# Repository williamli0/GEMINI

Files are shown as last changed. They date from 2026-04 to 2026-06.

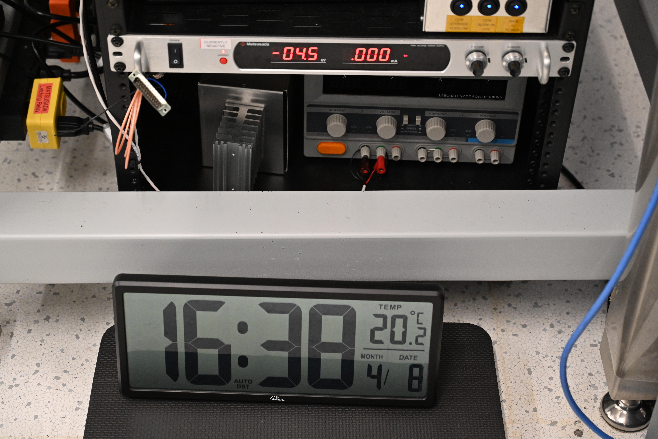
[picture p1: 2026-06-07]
GEMINI-Documents/GEMINI-HV Qualification Testing/260408 Afternoon 4.5 kV/DSC_4537.JPG

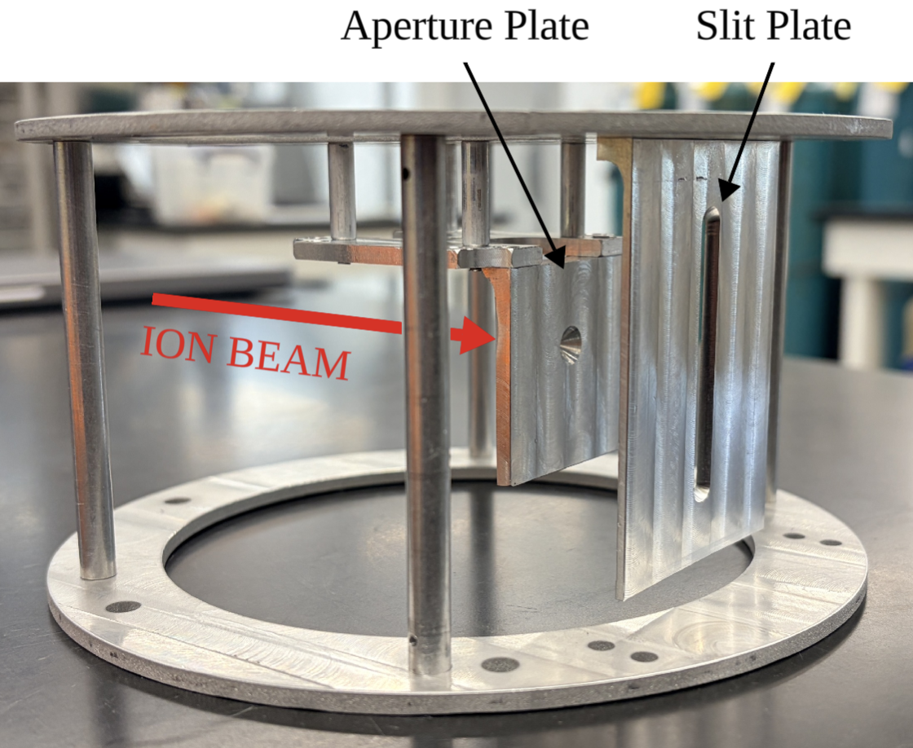
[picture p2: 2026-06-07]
GEMINI-Documents/GEMINI-Photos/GEMINI-JP_Report2Figures/slitPlateMounted.png

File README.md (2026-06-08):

In the SolidWorks folder, GEMINI-00-00-00.SLDASM is the master file that should be opened.

Getting around:

Final reports ("GEMINI-Fall_JP_CORRECTED.pdf" and "WilliamLiMAE399Spring2026Report_File.pdf"), PDR ("Fall 2025 GEMINI PDR.pdf"), and a scan of my engineering notebook ("GEMINI-Notebook") can be found in "GEMINI-Documents"

GEMINI-MATLAB contains the data processing file for GEMINI data: "GEMINIDataPipeline.m"

GEMINI-SIMION contains all the relevant SIMION files for the GEMINI Instrument

GEMINI-Solidworks contains all the necessary CAD files for GEMINI. There are some extraneous files for fasteners and old parts that were not used in the final version.

GEMINI-Drawings contains PDFs of the engineering drawings that were used to manufacture GEMINI.

In "GEMINI-Data", "GEMINI_FirstLightTestPlan.xlsx" contains the test record of two days of GEMINI data collection (configuration of the instrument, beam, notes, etc.). The gain curve file is "MCP Gain Curve Table.docx" found in "JP_Day1_Results" -> "William's GEMINI"

In "GEMINI-Data", "JP_Testing_FullDay1" and "JP_Testing_FullDay1" contain a folder with .csv files from the MCP that should be pointed to in MATLAB for processing. They also contain a folder with the .png output graphs from running the "GEMINIDataPipeline.m" Matlab file.

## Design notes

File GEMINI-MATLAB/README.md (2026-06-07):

GEMINIDataPipeline.m is the main file for processing GEMINI data. It takes in .csv files outputted by the Quantar MCP and outputs the actual visual output of the MCP.

Ensure that the .csv files being processed are on the current Matlab path.

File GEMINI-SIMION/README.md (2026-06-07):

To simulate an electrode in SIMION, a potential array (PA) must be created, either graphically or by means of coding a .GEM file

A .GEM file is the preferred method of creating electrodes because the graphical method is limited to planar, rectangular, or circular symmetry

A .GEM file gives full control over the location and shape of electrodes

After opening SIMION, click "New PA" and "From .GEM File"

Click "Save" and rename the file with extension .pa# which creates a separate numbered .pa file for each electrode programmed in the .GEM file

Click "Refine"

Click "Fast Adjust" to assign voltages to each PA

Then click "View/Open Ion Workbench" and the model is ready to be simulated.

In the .fly2 file, there is a variable at the top of the file that allows you to change the beam energy. It doesn't show up in SIMION when you try to edit the .fly2 file as text so you have to open the .fly2 file in something like Notepad to change the beam energy.

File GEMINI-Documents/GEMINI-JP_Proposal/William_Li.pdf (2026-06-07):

William Li
MAE398 Fall 2025
Adviser: Jamie Rankin

GEMINI: Graphene-Foil Electron-Emission Measurement Investigation for Novel Instrumentation

In space physics, amorphous carbon foils are a standard tool in particle-detecting space instruments because they release secondary electrons when struck by an incident particle. These secondary electrons can be used to make coincidence or time-of-flight (TOF) measurements, which are used by scientists to deduce properties of the incident particle such as mass, species, and energy. However, little is known, beyond a handful of published experiments, about exactly how the process of secondary electron emission works and how foil thickness and composition affect the fluence and energy of secondary electrons.
To address this gap, this proposal aims to develop an ultra-high-vacuum (UHV) compatible scientific instrument that examines the effect of foil thickness and composition on secondary electron emission in a laboratory setting. This laboratory instrument will position a carbon-based foil in a particle beam to measure incident and secondary particles and separate the transmitted particles by charge state. The instrument will be designed based on an existing device built by students in Princeton’s 2023-2024 AST250/251 Space Physics Lab class, which was used to image carbon foils in the path of an ion beam and quantify the number of holes and wrinkles (defects) in the foil and their effect on its performance . The new instrument created as part of this research, GEMINI – which stands for Graphene-Foil Electron-Emission Measurement Investigation for Novel Instrumentation – will hold at least three carbon-based foils, concentrically partition charges, and measure secondary electron emission from the foils, allowing the instrument operator to characterize and perform side-by-side comparisons of amorphous carbon and few-layer-graphene (FLG) foils under the same particle beam. The end scientific goal of this research is to create an empirical model that infers foil thickness and composition based on the fluence and energy of secondary electrons emitted from the foil when it is placed in an incident particle beam.
In current literature it is hypothesized that the thinner the foil, the more sensitive a space instrument will be to detecting higher mass and lower energy particles, so a graphene foil, as a single layer of carbon, is expected to perform significantly better than amorphous carbon. However, existing experimentally-based findings in the literature do not support that theory and show that graphene only has marginal improvements over amorphous carbon. In addition to the carbon layer thickness, it is hypothesized that there is a “crud layer” of water vapor and other trace elements that accumulates on both types of carbon-based foils which significantly increases the thickness and negates the supposed benefits of a thinner foil. The development of GEMINI, will therefore, hold tremendous scientific value. It will mark the first ever study of secondary electron emission as a function of graphene foil thickness and composition and will allow future researchers to reliably characterize different carbon-based foils with varying thicknesses and surface compositions in a laboratory setting, in search for the optimal candidates for space flight. As previously mentioned, GEMINI will build upon an apparatus first designed by the 2023-2024 AST250/251 class. The class’s instrument uses three linear actuators to move a pinhole and carbon foil in front of a microchannel plate (MCP) imager so that when the device is placed in line with a beam of particles in the Space Physics Lab’s vacuum chamber, the MCP

William Li
MAE398 Fall 2025
Adviser: Jamie Rankin

creates a 2D spatial map of particle counts. It also has a metal gate (consisting of 2 parallel rods) that can be energized to high voltage and serves as an electrostatic analyzer (ESA), deflecting particles based on their energy and/or charge. This creates a visual distribution on the MCP which can be used to quantify how many of the particles are negatively charged, positively charged, or neutral, which in turn provides information on the composition of the foil.
Building upon the AST250/251 design, to meet the goals of this research, a channel electron multiplier (CEM) and new electro-optical components will be added to the design to measure the energy and fluence of secondary electrons emitted from the foil. CEMs multiply 1 electron to ~107-108 electrons, essentially creating a cascade of electrons with enough charge to be turned into a detectable signal. Adding a CEM directly contributes to the science goals of GEMINI, as it allows us to investigate how the foil thickness and composition affect the energy and fluence of secondary electron emission as the incident particles interact with the foil. GEMINI also fixes some mechanical flaws with the AST250/251 design, primarily related to the linear actuation method, which cannot precisely control the position of the pinhole and carbon foils as intended and is prone to getting stuck, making the device unreliable. The entire device is also tilted at a 45-degree angle to facilitate retraction of the linear actuators which are only controllable in the extending direction. However, this poses challenges for experimental reproducibility and needs to be re-examined.
For this project, SolidWorks CAD software will be used to mechanically design GEMINI and files from SolidWorks will be exported to Ansys for analysis and SIMION for electro-optical simulations. From an educational development perspective, this independent research is an opportunity to improve CAD skills, specifically in Design for Manufacturing (DFM). This project is also an opportunity to learn how to perform simulations in Ansys, including, but not limited to structural FEA and thermal simulations. Lastly, the project will also provide experience with SIMION, specifically in verifying simulation results by comparing them to collected data.
In total, the project duration spans both the Fall 2025 and Spring 2026 semesters. For Fall 2025 the requirements for this project are to (1) complete the redesign of the existing AST250/251 class instrument, (2) achieve a 15% reduction in mass without increasing the volume of the instrument, and (3) test the instrument and achieve a reliability of 10 cumulative hours in a beamline without a fault. In Spring 2026, with GEMINI built, the focus of the research will shift to taking scientific measurements of amorphous carbon foils and FLGs and creating the model that connects the foil’s thickness and composition properties to the data collected by the instrument. The foils will then be taken to Princeton’s Imaging and Analysis Center (IAC) for foil thickness and composition measurements, in order to quantify the agreement between the model and IAC measurements, with a goal of achieving agreement to within 10%. In terms of project management, this project involves a weekly advisor-student meeting to ensure continuous satisfactory progress, attendance at the Space Physics Lab weekly standup at 8AM on the first day of the week, and scheduled time to work in the lab from 1PM-5PM on Thursdays and 8:30AM-5PM on Fridays.

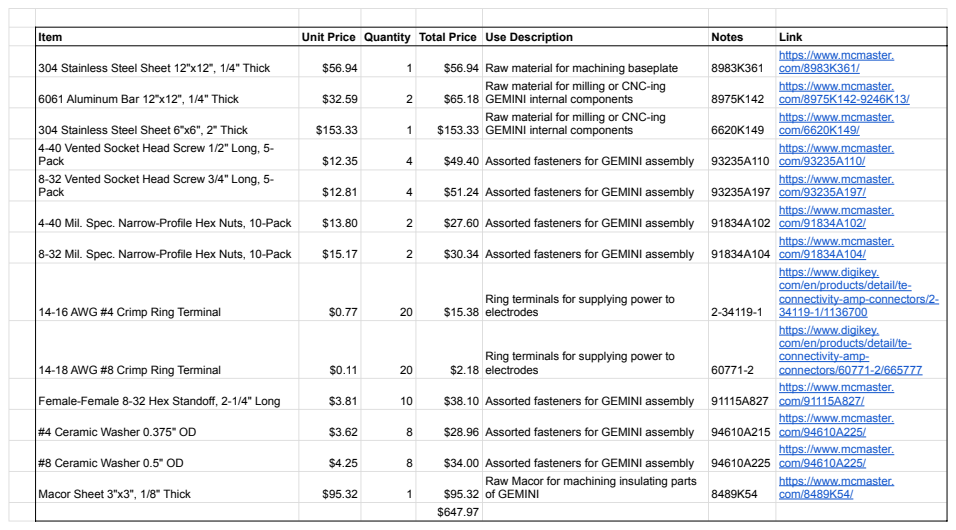
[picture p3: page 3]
Item; Unit Price Quantity Total Price Use Description; Notes; Link; 304 Stainless Steel Sheet 12"x12", 1/4" Thick; $56.94 Raw material for machining baseplate; 6061 Aluminum Bar 12"x12", 1/4" Thick; GEMINI internal components; 304 Stainless Steel Sheet 6"x6", 2" Thick; Pack; $49.40 Assorted fasteners for GEMINI assembly; $51.24 Assorted fasteners for GEMINI assembly; 4-40 Mil. Spec. Narrow-Profile Hex Nuts, 10-Pack; $27.60 Assorted fasteners for GEMINI assembly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

https://www.mcmaster.
com/8983K361/ (https://www.mcmaster.com/8983K361/)
com/8975K142-9246K13/ (https://www.mcmaster.com/8975K142-9246K13/)
com/6620K149/ (https://www.mcmaster.com/6620K149/)
com/93235A110/ (https://www.mcmaster.com/93235A110/)
com/93235A197/ (https://www.mcmaster.com/93235A197/)
com/91834A102/ (https://www.mcmaster.com/91834A102/)
com/91834A104/ (https://www.mcmaster.com/91834A104/)
https://www.digikey.
com/en/products/detail/te-
connectivity-amp-connectors/2-
connectivity-amp-
connectors/60771-2/665777 (https://www.digikey.com/en/products/detail/te-connectivity-amp-connectors/60771-2/665777)
com/91115A827/ (https://www.mcmaster.com/91115A827/)
com/94610A225/ (https://www.mcmaster.com/94610A225/)
com/8489K54/ (https://www.mcmaster.com/8489K54/)

Raw material for milling or CNC-ing

4-40 Vented Socket Head Screw 1/2" Long, 5-
8-32 Vented Socket Head Screw 3/4" Long, 5-

Ring terminals for supplying power to

Raw Macor for machining insulating parts

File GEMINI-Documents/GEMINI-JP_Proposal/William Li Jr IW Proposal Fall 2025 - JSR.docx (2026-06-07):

GEMINI: Graphene-Foil Electron-Emission Mapping Investigation for Novel Instrumentation

In space physics, amorphous carbon foils are a standard tool in particle-detecting space instruments because they release secondary electrons when struck by an incident particle. These secondary electrons can be used to make coincidence or time-of-flight (TOF) measurements, which are used by scientists to deduce properties of the incident particle such as mass, species, and energy. However, little is known beyond a handful of published experiments, about exactly how the process of secondary electron emission works and how foil thickness and composition affect the fluence of secondary electrons.

To address this gap, this proposal aims to develop an ultra-high-vacuum (UHV) compatible scientific instrument that holds a carbon foil in the path of a particle beam and partitions particles passing through the foil based on charge state while measuring the fluence of secondary electrons emitted from the carbon foil as it interacts with the beam. The instrument will be designed based on an existing device built by students in the 2023-2024 AST250/251 class which was used to image carbon foils in the path of an ion beam and quantify the effect of holes and wrinkles (defects) in the foil on its performance. The new instrument created as part of this research will hold at least three carbon-based foils, concentrically partition charges, and measure secondary electron emission from the foils allowing the instrument operator to measure the effect of different types of foils, such as amorphous carbon foils and few-layer-graphene foils (FLGs) under the same particle beam. The end scientific goal of this research is to create an empirical model that infers the thickness and composition of the measured carbon-based foil based on the fluence of secondary electrons emitted from the foil.

In current literature it is hypothesized that the thinner the foil, the more sensitive a space instrument will be to detecting higher mass particles and lower energy particles, so a graphene foil, as a single layer of carbon, should perform significantly better than amorphous carbon. However, existing experimentally-based findings in the literature does not support that theory and shows that graphene only has marginal improvements over amorphous carbon. It is hypothesized that there is a “crud layer” of water vapor and other trace elements that accumulates on carbon-based foils which significantly increases the thickness and erases the supposed benefits of a thinner foil. In a laboratory setting, future researchers can use GEMINI to test different graphene foils with varying thicknesses and surface compositions to search for the optimal graphene foil for space flight. The development of GEMINI holds tremendous scientific value. It will mark the first ever study of secondary electron emission as a function of graphene foil thickness and composition and thus will inform the qualification of graphene foils as the next generation of carbon foils in space instruments.

As previously mentioned, this project will build upon an apparatus first designed by the 2023-2024 AST250/251 class in the Space Physics Lab. The class’s instrument uses three linear actuators to move a pinhole and carbon foil in front of a microchannel plate (MCP) imager so that when the device is placed in line with a beam of particles in the Space Physics Lab’s vacuum chamber, the MCP creates a 2D spatial map of particle counts. It also has a metal gate (consisting of 2 parallel rods) that can be energized to high voltage and serves as an electrostatic analyzer (ESA), deflecting particles based on their energy and charge. This creates a visual distribution on the MCP which can be used to quantify how many of the particles emitted from the foil came off as negatively charged, positively charged, or neutral, as well as how much charge they carried (+1, +2, etc.). The ESA gate can also filter out particles to only look at one specific energy at a time.

There are some flaws with the AST250/251 design that primarily relate to the actuation method, which cannot precisely control the position of the pinhole and carbon foils as intended and is prone to getting stuck, making the device unreliable. The entire device is also tilted at a 45-degree angle to facilitate retraction of the linear actuators which are only controllable in the extending direction, which poses challenges for experimental reproducibility and also needs to be re-examined. GEMINI will improve upon the AST250/251 instrument mechanically by implementing a different actuation mechanism, possibly a rotating wheel rather than linear actuators. A new concentric ESA will also be designed to replace the existing metal gate ESA because the metal gate design shapes the paths of ions in a rectangular pattern, resulting in lost data when the particles collide with the MCP which has a circular aperture. Building upon the AST250/251 design, to meet the goals of this research, a channel electron multiplier (CEM) and new ion optics will be added to the design to take secondary electron measurements. CEMs multiply 1 electron to ~10⁷-10⁸ electrons, essentially creating a cascade of electrons with enough charge to be turned into a detectable signal.

For this project, SolidWorks CAD software will be used to mechanically design GEMINI and files from SolidWorks will be exported to Ansys for analysis and SIMION for electro-optical simulations. From an educational development perspective, this independent research is an opportunity to improve CAD skills, specifically in Design for Manufacturing (DFM). This project is also an opportunity to learn how to perform simulations in Ansys, including, but not limited to structural FEA and thermal simulations. Lastly, the project will also provide experience with SIMION, specifically in verifying simulation results by comparing them to collected data.

In total, the project duration spans both the Fall 2025 and Spring 2026 semesters. For Fall 2025 the requirements for this project are to (1) complete the redesign of the existing AST250/251 class instrument, (2) achieve a 15% reduction in mass without increasing the volume of the instrument, and (3) test the instrument and achieve a reliability of 10 cumulative hours in a beamline without a fault. In Spring 2026, with the instrument built, the focus of the research will shift to taking scientific measurements of amorphous carbon foils and FLGs and creating the model that connects the foil’s thickness and composition properties to the data collected by the instrument. The foils will then be taken to Princeton’s Imaging and Analysis Center (IAC) for foil thickness and composition measurements, in order to quantify the agreement between the model and IAC measurements, with a goal of achieving agreement to within 10%.

In terms of project management, this research involves a weekly advisor-student meeting to ensure continuous satisfactory progress, attendance at the Space Physics Lab weekly standup at 8AM on the first day of the week, and scheduled time to work in the lab from 1PM-5PM on Thursdays and 8:30AM-5PM on Fridays.

William Li MAE398, Fall 2025 Adviser: Jamie Rankin

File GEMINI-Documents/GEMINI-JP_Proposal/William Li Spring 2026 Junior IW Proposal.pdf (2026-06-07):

William Li
MAE399 Spring 2026
Adviser: Jamie Rankin

GEMINI: Graphene-Foil Electron-Emission Measurement Investigation for Novel Instrumentation

Amorphous carbon foils (~20-30 atomic layers in thickness) are a crucial piece of any scientific space instrument that seeks to study the solar wind or other particles present in the solar system. This is because carbon foils possess the property of releasing a secondary electron when struck by an incident particle, usually an ion. This secondary electron can be used to make coincidence or time-of-flight (TOF) measurements, which, combined with other parameters, enables scientists to deduce properties of the incident particle such as the mass, species, and energy. However, carbon foils also affect the incident particle in undesirable ways, by causing angular scattering and energy loss of the particle. It is theorized that thinner foils are able to detect lower energy particles and higher mass particles because they reduce angular scattering and energy loss, but the exact relationship between foil thickness and these other properties are not well understood. For example, previous studies have shown that the proportionality between foil thickness and angular scattering is different for carbon foils and graphene (a single atomic layer of carbon) foils, but these studies did not explore energies lower than 3 keV. In the Fall 2025 semester, the GEMINI instrument was designed to measure angular scattering and secondary electron emission of carbon and graphene foils at energies ranging from 200 eV to 2.5 keV. This Spring 2026 independent work is a continuation of the work completed in Fall 2025. This proposal for Spring 2026 independent work proposes placing the GEMINI instrument in the Science Vacuum Chamber in the Princeton Space Physics Lab and exposing it to a variety of ion beams to gather data on the energy and yield of secondary electrons from graphene and carbon foils at ion beam energies of 200 eV to 2.5 keV. This fills a gap in existing literature exploring the angular scattering and secondary electron emission of graphene foils at low energy ion beams. The scope of work for the Spring 2026 semester includes machining the components of GEMINI, physically assembling it, and testing it in vacuum in the Space Physics Lab. For testing, GEMINI was designed to hold three carbon or graphene foils at once so that direct comparisons can be made between the different foils without having to remove the instrument from the vacuum chamber. Essentially, an identical ion beam can be used to study three different foils. For this semester, the three foils that will be tested in GEMINI are a graphene foil, 0.6 μg/cm² carbon foil, and 1.1 μg/cm² carbon foil. Each of the foils will be exposed to an ion beam of energies ranging from 200 eV to 2.5 keV in 100 eV increments. The beam compositions that will be tested are H

+
, H2

+

, He⁺

, and Ar⁺
. The scope of work for Spring 2026 also encompasses developing a data collection and processing pipeline for GEMINI. This involves writing LabVIEW code to automate the process of imaging each of the three foils on GEMINI with different beam compositions and energies. MATLAB will be used to process the data from GEMINI’s primary sensor, the imaging microchannel plate (MCP).
Long-term, the goal is to continue using GEMINI to contribute to heliophysicists’ understanding of graphene foils by modifying the thickness and composition of graphene foils on the molecular scale and studying how different modifications affect angular scattering, energy loss, and secondary electron emission from graphene foils. This is future research that will be pursued in the 2026-2027 academic year.

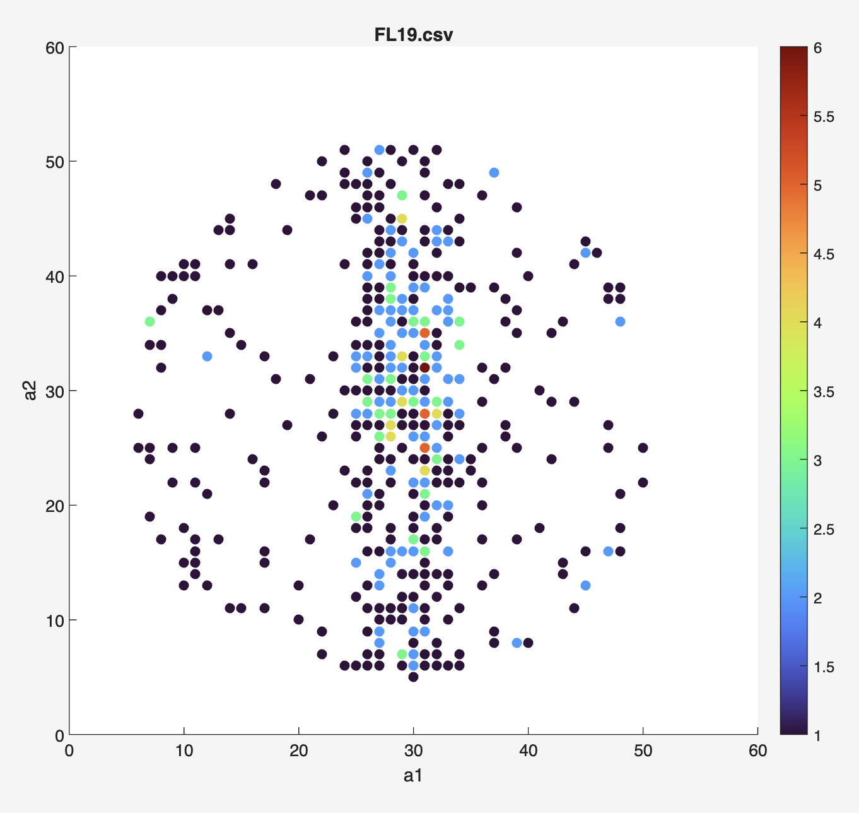
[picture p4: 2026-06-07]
GEMINI-Documents/GEMINI-Photos/GEMINI-JP_Report2Figures/Screenshot 2026-04-23 at 14.20.40.png

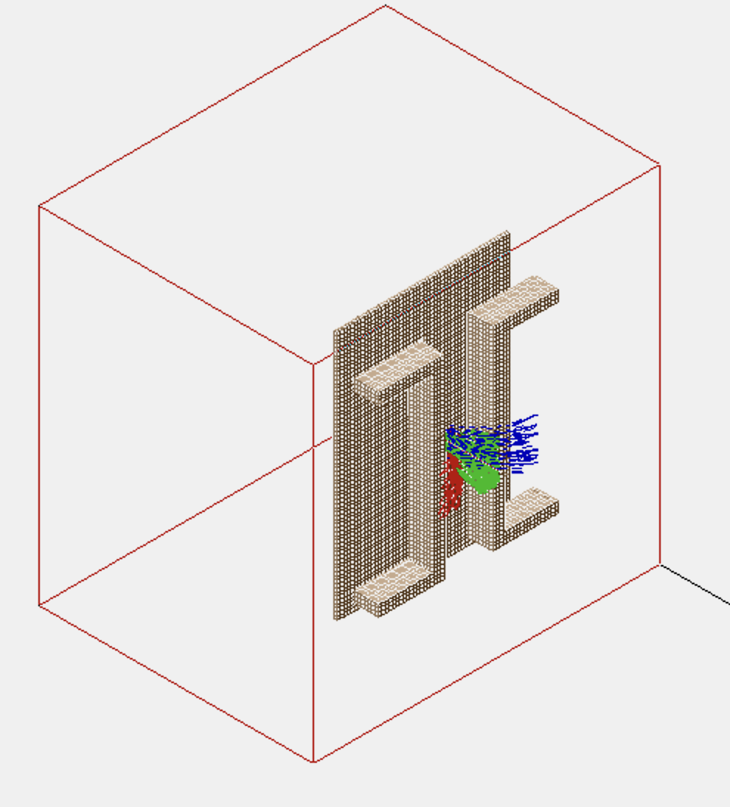
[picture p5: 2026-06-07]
GEMINI-Documents/GEMINI-Photos/GEMINI-JP_Report2Figures/500eV_600V_p_Iso.png

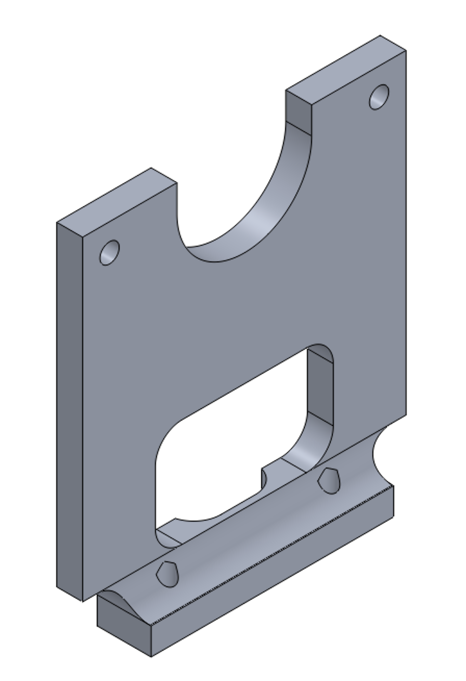
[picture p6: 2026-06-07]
GEMINI-Documents/GEMINI-Photos/GEMINI-JP_Report2Figures/Screenshot 2026-04-28 at 16.29.42.png

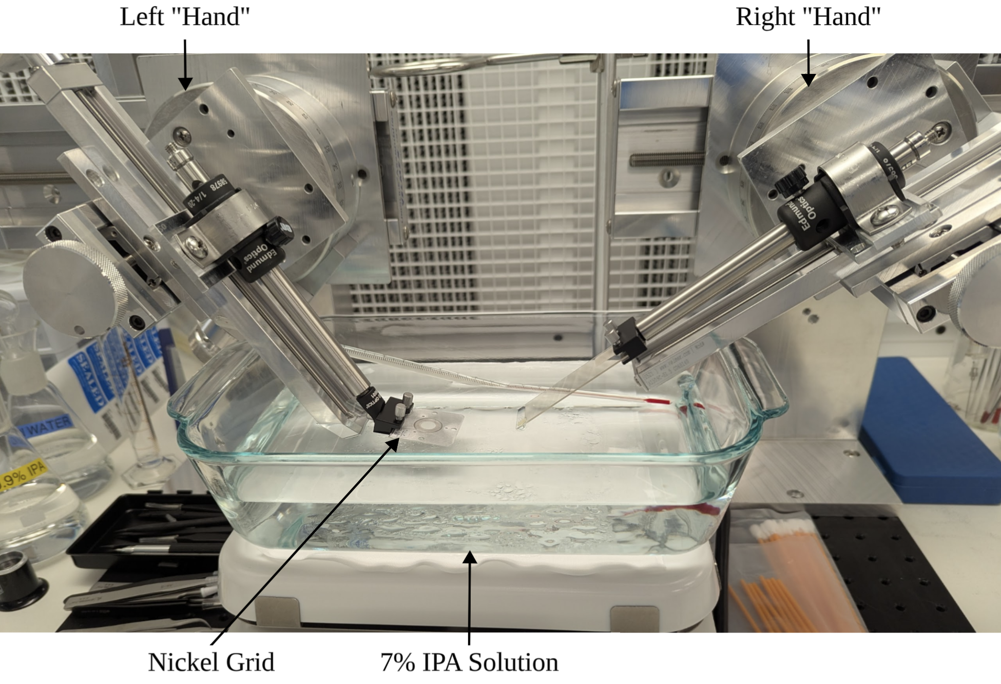
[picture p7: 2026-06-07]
GEMINI-Documents/GEMINI-Photos/GEMINI-JP_Report2Figures/floatApparatus.png

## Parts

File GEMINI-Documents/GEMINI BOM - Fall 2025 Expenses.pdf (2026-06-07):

# GEMINI Bill of Materials

ITEM
NO.

PART

| NO. | DESCRIPTION | ORDER
| | | QTY | UNIT
| | | | PRICE | TOTAL
| | | | | PRICE | DATE
| | | | | | ORDERED | COMMENTS
1 | 93505A027 | 10-32, 1-1/4" Long Male-Female Hex
| | Standoff | 5 | $1.38 | $6.90 | 12/8/25
2 | 92510A648 | #10 7/8" Long Aluminum Unthreaded Spacer | 5 | $1.74 | $8.70 | 12/8/25
3 | 93330A541 | 4-40, 3" Long, Aluminum Female-Female
| | Round Standoff | 4 | $1.52 | $6.08 | 12/8/25 | Roof Mounting to Upper Outer Skirt
4 | 94335A115 | 6-32, 1/2" Long, Glazed L5 Ceramic Female-
| | Female Round Standoff | 4 | $5.65 | $22.60 | 12/8/25 | Deflector Plate Mounting Standoffs
5 | Shipping 1 | Shipping to E-Quad Loading Dock | 1 | $9.21 | $0.00 | 12/8/25
6 | 89015K259 | 6061 Aluminum Sheet 0.160" Thick, 8" x 8" | 4 | $19.49 | $77.96 | 1/28/26 | Roof, Upper Outer Skirt
7 | 89015K255 | 6061 Aluminum Sheet 0.160" Thick, 6" x 6" | 1 | $12.47 | $12.47 | 1/28/26 | Inner Skirt
8 | 89155K221 | Oversized 6061 Aluminum Sheet 1/4" Thick, 8" x 8" | 2 | $17.06 | $34.12 | 1/28/26 | All other parts except Deflector Plates
9 | 8975K613 | 6061 Aluminum Bar 5/16" Thick x 1" Wide x 12'' Long | 1 | $4.18 | $4.18 | 1/28/26 | 3.6'' required. Deflector Plates. Ordered 8976K856 (same)
10 | 92196A103 | 4-40, 1/8" Long, 18-8 SS Socket Head Screw. Pack of 100 | 1 | $6.10 | $6.10 | 1/28/26 | Shield mounting and Deflector Plate power.
11 | 90550A122 | M4 x 0.7 mm, 10 mm Long, 18-8 SS Vented Flat Head Screw. Pack of 5 | 1 | $13.10 | $13.10 | 1/28/26 | Inner Skirt mounting to Rotational Stage
12 13 | 93330A541 94335A115 | 4-40, 3" Long, Aluminum Female-Female Round Standoff | 2 | $2.17 | $4.34 | 1/28/26 | Roof Mounting to Upper Outer Skirt
| | 6-32, 1/2" Long, Glazed L5 Ceramic Female-Female Round Standoff | 2 | $5.65 | $11.30 | 1/28/26 | Deflector Plate Mounting Standoffs
14 | 92510A460 | #8, 1/8" Long Aluminum Unthreaded Spacer | 8 | $0.37 | $2.96 | 1/28/26 | For raising Inner Skirt
15 | 88805A27 | 1/4" Ball End Mill, Uncoated Carbide, 4 Flute, 2-1/2" Overall Length | 1 | $20.85 | $20.85 | 1/28/26 | For machining fillets
16 | 2739A38 | 90 Degree Fluteless Smooth-Finish Countersink | 1 | $15.40 | $15.40 | 1/28/26 | For Inner Skirt M4 countersinks
17 | 2739A33 | 82 Degree Fluteless Smooth-Finish Countersink | 1 | $15.40 | $15.40 | 1/28/26 | For all other countersinks
18 | 92210A105 | 4-40, 1/4" Long, 18-8 SS Flat Head Screw 82 Degree Countersink. Pack of 100 | 1 | $4.43 | $4.43 | 1/28/26 | Workhorse. Standard fastener for most of GEMINI
19 | 91292A322 | M5 x 0.8 mm, 110 mm Long, 18-8 SS Socket Head Screw. Pack of 10 | 1 | $11.03 | $11.03 | 1/28/26 | For mounting Upper Outer Skirt to Rotational Stage
20 | Shipping 2 | Shipping to E-Quad Loading Dock | 1 | $12.10 | $0.00 | 1/28/26
21 | 8974K105 | 6061 Aluminum Rod 3/16" Diameter x 1/2 Foot Long | 1 | $1.60 | $1.60 | 1/29/26 | 0.687'' each (x4). Dummy hardware for when motor is detached. Ordered 8974K21 (same)
22 | 92125A138 | M3 x 0.5 mm, 25 mm Long, 18-8 SS Flat Head Screw. Pack of 100 | 1 | $11.38 | $11.38 | 1/29/26 | Require 4. Dummy hardware for when motor is detached
23 | 93033A107 | M3 x 0.5 mm 18-8 SS Flange Nut. Pack of 100 | 1 | $7.33 | $7.33 | 1/29/26 | For mounting D42.1 Motor
24 | 91979A207 | 2-56, 1/8" Long, 18-8 SS Set Screw. Pack of 10 | 1 | $6.79 | $6.79 | 1/29/26 | For Aperture Rotation Plate
25 | 92510A435 | #12, 2-1/4" Long Aluminum Unthreaded Spacer | 5 | $7.73 | $38.65 | 1/29/26 | For mounting Upper Outer Skirt to Rotational Stage
26 | Shipping 3 | Shipping to E-Quad Loading Dock | 1 | $10.18 | $0.00 | 1/29/26
TOTAL: | $343.67

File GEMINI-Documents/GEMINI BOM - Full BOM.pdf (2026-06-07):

# GEMINI Bill of Materials

ITEM NO. | PART NO. | DESCRIPTION | REQ. QTY | ORDER QTY | UNIT PRICE | TOTAL PRICE | COMMENTS
1 | 89015K259 | 6061 Aluminum Sheet 0.160" Thick, 8" x 8" | 3 | 4 | $19.49 | $77.96 | Roof, Upper Outer Skirt
2 | 89015K255 | 6061 Aluminum Sheet 0.160" Thick, 6" x 6" | 1 | 1 | $12.47 | $12.47 | Inner Skirt
3 | 89155K221 | Oversized 6061 Aluminum Sheet 1/4" Thick, 8" x 8" | 1 | 2 | $17.06 | $34.12 | All other parts except Deflector Plates
4 | 8975K613 | 6061 Aluminum Bar 5/16" Thick x 1" Wide x 12'' Long | 1 | 1 | $4.18 | $4.18 | 3.6'' required. Deflector Plates. Ordered 8976K856 (same)
5 | 92196A103 | 4-40, 1/8" Long, 18-8 SS Socket Head Screw. Pack of 100 | 14 | 1 | $6.10 | $6.10 | Shield mounting and Deflector Plate power.
6 | 90550A122 | M4 x 0.7 mm, 10 mm Long, 18-8 SS Vented Flat Head Screw. Pack of 5 | 4 | 1 | $13.10 | $13.10 | Inner Skirt mounting to Rotational Stage
7 | 93330A541 | 4-40, 3" Long, Aluminum Female-Female Round Standoff | 4 | 6 | $2.17 | $13.02 | Roof Mounting to Upper Outer Skirt. Ordered 4 on 12/8/25
8 | 94335A115 | 6-32, 1/2" Long, Glazed L5 Ceramic Female-Female Round Standoff | 4 | 6 | $5.65 | $33.90 | Deflector Plate Mounting Standoffs. Ordered 4 on 12/8/25
9* | 7113K148 | 22-18 Wire Gauge, #4 Screw Size, Tin-Plated Copper Ring Terminals Noninsulated. Pack of 100 | 2 | 1 | $16.02 | $16.02 | Power delivery to Deflector Plates.
10* | 92210A077 | 2-56, 1/4" Long, 18-8 SS Flat Head Screw 82 Degree Countersink. Pack of 100 | 4 | 1 | $5.83 | $5.83 | For mounting Aperture Plates
11* | 92210A105 | 4-40, 1/4" Long, 18-8 SS Flat Head Screw 82 Degree Countersink. Pack of 100 | 18 | 1 | $4.43 | $4.43 | Workhorse. Standard fastener for most of GEMINI. Ordered anyways (unsure of lab qty)
12* | 93235A144 | Vented Socket Head Screw 6-32 Thread Size, 1/4" Long. Pack of 5 | 8 | 2 | $5.97 | $11.94 | For Deflector Plate ceramic standoffs
13 | 92510A460 | #8, 1/8" Long Aluminum Unthreaded Spacer | 4 | 8 | $0.38 | $3.04 | For raising Inner Skirt
14 | 8974K105 | 6061 Aluminum Rod 3/16" Diameter x 1/2 Foot Long | 1 | 1 | $1.60 | $1.60 | 0.687'' each (x4). Dummy hardware for when motor is detached. Ordered 8974K21 (same)
15 | 92125A138 | M3 x 0.5 mm, 25 mm Long, 18-8 SS Flat Head Screw. Pack of 100 | 4 | 1 | $11.38 | $11.38 | Require 4. Dummy hardware for when motor is detached
16 | 8803A383 | 0.1985" Reamer, High-Speed Steel | 1 | 1 | $24.52 | $24.52 | For creating Aperture Rotation Plate collar hole
17 | 93033A107 | M3 x 0.5 mm 18-8 SS Flange Nut. Pack of 100 | 4 | 1 | $7.33 | $7.33 | For mounting D42.1 Motor
18 | 91979A207 | 2-56, 1/8" Long, 18-8 SS Set Screw. Pack of 10 | 1 | 1 | $6.79 | $6.79 | For Aperture Rotation Plate
19 | 92510A435 | #12, 2-1/4" Long Aluminum Unthreaded Spacer | 5 | 5 | $7.73 | $38.65 | For mounting Upper Outer Skirt to Rotational Stage
20 | 91292A322 | M5 x 0.8 mm, 110 mm Long, 18-8 SS Socket Head Screw. Pack of 10 | 5 | 1 | $11.03 | $11.03 | For mounting Upper Outer Skirt to Rotational Stage
21 | 88805A27 | 1/4" Ball End Mill, Uncoated Carbide, 4 Flute, 2-1/2" Overall Length | 1 | 1 | $20.85 | $20.85 | For machining fillets
22 | 2739A38 | 90 Degree Fluteless Smooth-Finish Countersink | 1 | 1 | $15.40 | $15.40 | For Inner Skirt M4 countersinks
23 | 2739A33 | 82 Degree Fluteless Smooth-Finish Countersink | 1 | 1 | $15.40 | $15.40 | For all other countersinks
TOTAL: | $389.06

* indicates part already exists in the Space Physics Lab

# GEMINI Bill of Materials (Continued)

OTHER COMPONENTS (INFRASTRUCTURE & NON-CRITICAL)

ITEM NO. | PART NO. | DESCRIPTION | REQ. QTY | ORDER QTY | UNIT PRICE | TOTAL PRICE | COMMENTS
23 | D42.1-H | AML UHV Stepper Motor. Dry, lubricated hybrid ceramic bearings | 1 | 1 | $1,080 | $1,080 | For rotating aperture plates
24 | SMD3 | AML Single-Axis Bipolar Stepper Motor Drive | 1 | 1 | $840 | $840 | For controlling D42.1-H motor
25* | 3394A | Quantar 2-Layer 40 mm MCP | 1 | 0 | N/A | N/A
26* | | MCP #0 Mounting Screws | 4 | 0 | N/A | N/A | For mounting MCP
27* | | RV120 Rotational Stage | 1 | 0 | N/A | N/A
28* | | CoDICE 0.9895'' Spacer | 1 | 0 | N/A | N/A
29* | | 0.010'' Thick Aluminum Shim Stock | 1 | 0 | N/A | N/A | For Shield and CoDICE Spacer Shim
30* | | SHV5 Connector | 2 | 0 | N/A | N/A
31* | | High Voltage insulated wiring | | 0 | N/A | N/A
32* | | High Voltage Power Supply | 2 | 0 | N/A | N/A | For Deflector Plates
33* | | Low Voltage Power Supply | 1 | 0 | N/A | N/A | For Deflector Plates measuring secondary electrons
TOTAL: | $1,920

* indicates part already exists in the Space Physics Lab

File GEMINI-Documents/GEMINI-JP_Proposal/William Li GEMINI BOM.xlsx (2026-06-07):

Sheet: Fall 2025
Item | Unit Price | Quantity | Total Price | Use Description | Notes | Link
304 Stainless Steel Sheet 12"x12", 1/4" Thick | $56.94 | 1 | $56.94 | Raw material for machining baseplate | 8983K361 | https://www.mcmaster.com/8983K361/
6061 Aluminum Bar 12"x12", 1/4" Thick | $32.59 | 2 | $65.18 | Raw material for milling or CNC-ing GEMINI internal components | 8975K142 | https://www.mcmaster.com/8975K142-9246K13/
304 Stainless Steel Sheet 6"x6", 2" Thick | $153.33 | 1 | $153.33 | Raw material for milling or CNC-ing GEMINI internal components | 6620K149 | https://www.mcmaster.com/6620K149/
4-40 Vented Socket Head Screw 1/2" Long, 5-Pack | $12.35 | 4 | $49.40 | Assorted fasteners for GEMINI assembly | 93235A110 | https://www.mcmaster.com/93235A110/
8-32 Vented Socket Head Screw 3/4" Long, 5-Pack | $12.81 | 4 | $51.24 | Assorted fasteners for GEMINI assembly | 93235A197 | https://www.mcmaster.com/93235A197/
4-40 Mil. Spec. Narrow-Profile Hex Nuts, 10-Pack | $13.80 | 2 | $27.60 | Assorted fasteners for GEMINI assembly | 91834A102 | https://www.mcmaster.com/91834A102/
8-32 Mil. Spec. Narrow-Profile Hex Nuts, 10-Pack | $15.17 | 2 | $30.34 | Assorted fasteners for GEMINI assembly | 91834A104 | https://www.mcmaster.com/91834A104/
14-16 AWG #4 Crimp Ring Terminal | $0.77 | 20 | $15.38 | Ring terminals for supplying power to electrodes | 2-34119-1 | https://www.digikey.com/en/products/detail/te-connectivity-amp-connectors/2-34119-1/1136700
14-18 AWG #8 Crimp Ring Terminal | $0.11 | 20 | $2.18 | Ring terminals for supplying power to electrodes | 60771-2 | https://www.digikey.com/en/products/detail/te-connectivity-amp-connectors/60771-2/665777
Female-Female 8-32 Hex Standoff, 2-1/4" Long | $3.81 | 10 | $38.10 | Assorted fasteners for GEMINI assembly | 91115A827 | https://www.mcmaster.com/91115A827/
#4 Ceramic Washer 0.375" OD | $3.62 | 8 | $28.96 | Assorted fasteners for GEMINI assembly | 94610A215 | https://www.mcmaster.com/94610A225/
#8 Ceramic Washer 0.5" OD | $4.25 | 8 | $34.00 | Assorted fasteners for GEMINI assembly | 94610A225 | https://www.mcmaster.com/94610A225/
Macor Sheet 3"x3", 1/8" Thick | $95.32 | 1 | $95.32 | Raw Macor for machining insulating parts of GEMINI | 8489K54 | https://www.mcmaster.com/8489K54/
 |  |  | $647.97

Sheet: Spring 2026
Item | Unit Price | Quantity | Total Price | Use Description | Notes | Link
 |  |  | $0.00
 |  |  | $0.00
 |  |  | $0.00
 |  |  | $0.00
 |  |  | $0.00
 |  |  | $0.00
 |  |  | $0.00
 |  |  | $0.00
 |  |  | $0.00
 |  |  | $0.00
 |  |  | $0.00
 |  |  | $0.00
 |  |  | $0.00
 |  |  | $0.00
 |  |  | $0.00
 |  |  | $0.00
 |  |  | $0.00

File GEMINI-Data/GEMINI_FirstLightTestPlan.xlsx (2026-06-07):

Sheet: Day 1 Test Plan
Date | Start Time (EST) | Stop Time (EST) | GEMINI Operator Name | Facility Operator Name | ACTIONS / STATUS | Filename | Converted Filename | Procedure/HV log | Test Objective | Foil | North Deflector Voltage (V) | South Deflector Voltage (V) | MCP Voltages (V) | IS Pressure (Torr) | IT Pressure (Torr) | Focus 1 | Focus 2 | Emission current (mA) | Ext (%) | Px (mm) | Py (mm) | Wien Filter Plate Potential | Energy | Ion Source Energy & Species | Helmholtz Coil Voltage (V) | Helmholtz Coil Current (A) | Helmholtz Coil Status (On/Off) | Rotational Stage (Axis 2) (deg) | Linear Stage (Axis 3) | SC Gate Valve | MC Gate Valve | Science Chamber Pressure (Torr) | Main Chamber Pressure (Torr) | Comments
 |  |  |  |  |  | GFL0 | GEMINI_p1000_FirstLight |  | First Light | None | +0 | +0 |  |  |  |  |  |  |  |  |  |  |  | 1 keV p+ |  |  | On | 0 | 0
 |  |  |  |  |  | p1 | GEMINI_p1000_N |  | 1 keV p+ Angular Scattering Baseline | None | +1084 | -+1084 |  |  |  |  |  |  |  |  |  |  |  | 1 keV p+ |  |  | On | 0 | 0
 |  |  |  |  |  | p2 | GEMINI_p1000_C |  | 1 keV p+ Carbon Angular Scattering | 1.1 ug/cm^2 | +1084 | -+1084 |  |  |  |  |  |  |  |  |  |  |  | 1 keV p+ |  |  | On | 54.12 | 0
 |  |  |  |  |  | p3 | GEMINI_p1000_G |  | 1 keV p+ Graphene Angular Scattering | Graphene | +1084 | -+1084 |  |  |  |  |  |  |  |  |  |  |  | 1 keV p+ |  |  | On | -54.12 | 0
 |  |  |  |  |  | p4 | GEMINI_p1250_N |  | 1.25 keV p+ Angular Scattering Baseline | None | +1355 | -+1355 |  |  |  |  |  |  |  |  |  |  |  | 1.25 keV p+ |  |  | On | 0 | 0
 |  |  |  |  |  | p5 | GEMINI_p1250_C |  | 1.25 keV p+ Carbon Angular Scattering | 1.1 ug/cm^2 | +1355 | -+1355 |  |  |  |  |  |  |  |  |  |  |  | 1.25 keV p+ |  |  | On | 54.12 | 0
 |  |  |  |  |  | p6 | GEMINI_p1250_G |  | 1.25 keV p+ Graphene Angular Scattering | Graphene | +1355 | -+1355 |  |  |  |  |  |  |  |  |  |  |  | 1.25 keV p+ |  |  | On | -54.12 | 0
 |  |  |  |  |  | p7 | GEMINI_p1500_N |  | 1.5 keV p+ Angular Scattering Baseline | None | +1626 | -+1626 |  |  |  |  |  |  |  |  |  |  |  | 1.5 keV p+ |  |  | On | 0 | 0
 |  |  |  |  |  | p8 | GEMINI_p1500_C |  | 1.5 keV p+ Carbon Angular Scattering | 1.1 ug/cm^2 | +1626 | -+1626 |  |  |  |  |  |  |  |  |  |  |  | 1.5 keV p+ |  |  | On | 54.12 | 0
 |  |  |  |  |  | p9 | GEMINI_p1500_G |  | 1.5 keV p+ Graphene Angular Scattering | Graphene | +1626 | -+1626 |  |  |  |  |  |  |  |  |  |  |  | 1.5 keV p+ |  |  | On | -54.12 | 0
 |  |  |  |  |  | p10 | GEMINI_p750_N |  | 750 eV p+ Angular Scattering Baseline | None | +813 | -+813 |  |  |  |  |  |  |  |  |  |  |  | 750 eV p+ |  |  | On | 0 | 0
 |  |  |  |  |  | p11 | GEMINI_p750_C |  | 750 eV p+ Carbon Angular Scattering | 1.1 ug/cm^2 | +813 | -+813 |  |  |  |  |  |  |  |  |  |  |  | 750 eV p+ |  |  | On | 54.12 | 0
 |  |  |  |  |  | p12 | GEMINI_p750_G |  | 750 eV p+ Graphene Angular Scattering | Graphene | +813 | -+813 |  |  |  |  |  |  |  |  |  |  |  | 750 eV p+ |  |  | On | -54.12 | 0
 |  |  |  |  |  | p13 | GEMINI_p_500_N |  | 500 eV p+ Angular Scattering Baseline | None | +542 | -+542 |  |  |  |  |  |  |  |  |  |  |  | 500 eV p+ |  |  | On | 0 | 0
 |  |  |  |  |  | p14 | GEMINI_p_500_C |  | 500 eV p+ Carbon Angular Scattering | 1.1 ug/cm^2 | +542 | -+542 |  |  |  |  |  |  |  |  |  |  |  | 500 eV p+ |  |  | On | 54.12 | 0
 |  |  |  |  |  | p15 | GEMINI_p500_G |  | 500 eV p+ Graphene Angular Scattering | Graphene | +542 | -+542 |  |  |  |  |  |  |  |  |  |  |  | 500 eV p+ |  |  | On | -54.12 | 0
 |  |  |  |  | Disconnect Deflector Plates from HVPS. Connect North Deflector to small blue LVPS | e1 | GEMINI_p1000_N_e |  | 500 eV p+ Secondary Electron Baseline | None | +5 | +0 |  |  |  |  |  |  |  |  |  |  |  | 500 eV p+ |  |  | On | 0 | 0
 |  |  |  |  |  | e2 | GEMINI_p1000_C_e |  | 500 eV p+ Carbon Secondary Electron | 1.1 ug/cm^2 | +5 | +0 |  |  |  |  |  |  |  |  |  |  |  | 500 eV p+ |  |  | On | 54.12 | 0
 |  |  |  |  |  | e3 | GEMINI_p1000_G_e |  | 500 eV p+ Graphene Secondary Electron | Graphene | +5 | +0 |  |  |  |  |  |  |  |  |  |  |  | 500 eV p+ |  |  | On | -54.12 | 0
 |  |  |  |  |  | e4 | GEMINI_p1250_N_e |  | 750 eV p+ Secondary Electron | None | +5 | +0 |  |  |  |  |  |  |  |  |  |  |  | 750 eV p+ |  |  | On | 0 | 0
 |  |  |  |  |  | e5 | GEMINI_p1250_C_e |  | 750 eV p+ Carbon Secondary Electron | 1.1 ug/cm^2 | +5 | +0 |  |  |  |  |  |  |  |  |  |  |  | 750 eV p+ |  |  | On | 54.12 | 0
 |  |  |  |  |  | e6 | GEMINI_p1250_G_e |  | 750 eV p+ Graphene Secondary Electron | Graphene | +5 | +0 |  |  |  |  |  |  |  |  |  |  |  | 750 eV p+ |  |  | On | -54.12 | 0
 |  |  |  |  |  | e7 | GEMINI_p1500_N_e |  | 1 keV p+ Secondary Electron Baseline | None | +5 | +0 |  |  |  |  |  |  |  |  |  |  |  | 1 keV p+ |  |  | On | 0 | 0
 |  |  |  |  |  | e8 | GEMINI_p1500_C_e |  | 1 keV p+ Carbon Secondary Electron | 1.1 ug/cm^2 | +5 | +0 |  |  |  |  |  |  |  |  |  |  |  | 1 keV p+ |  |  | On | 54.12 | 0
 |  |  |  |  |  | e9 | GEMINI_p1500_G_e |  | 1 keV p+ Graphene Secondary Electron | Graphene | +5 | +0 |  |  |  |  |  |  |  |  |  |  |  | 1 keV p+ |  |  | On | -54.12 | 0
 |  |  |  |  |  | e10 | GEMINI_p750_N_e |  | 1.25 keV p+ Secondary Electron Baseline | None | +5 | +0 |  |  |  |  |  |  |  |  |  |  |  | 1.25 keV p+ |  |  | On | 0 | 0
 |  |  |  |  |  | e11 | GEMINI_p750_C_e |  | 1.25 keV p+ Carbon Secondary Electron | 1.1 ug/cm^2 | +5 | +0 |  |  |  |  |  |  |  |  |  |  |  | 1.25 keV p+ |  |  | On | 54.12 | 0
 |  |  |  |  |  | e12 | GEMINI_p750_G_e |  | 1.25 keV p+ Graphene Secondary Electron | Graphene | +5 | +0 |  |  |  |  |  |  |  |  |  |  |  | 1.25 keV p+ |  |  | On | -54.12 | 0
 |  |  |  |  |  | e13 | GEMINI_p_500_N_e |  | 1.5 keV p+ Secondary Electron Baseline | None | +5 | +0 |  |  |  |  |  |  |  |  |  |  |  | 1.5 keV p+ |  |  | On | 0 | 0
 |  |  |  |  |  | e14 | GEMINI_p_500_C_e |  | 1.5 keV p+ Carbon Secondary Electron | 1.1 ug/cm^2 | +5 | +0 |  |  |  |  |  |  |  |  |  |  |  | 1.5 keV p+ |  |  | On | 54.12 | 0
 |  |  |  |  |  | e15 | GEMINI_p500_G_e |  | 1.5 keV p+ Graphene Secondary Electron | Graphene | +5 | +0 |  |  |  |  |  |  |  |  |  |  |  | 1.5 keV p+ |  |  | On | -54.12 | 0

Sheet: Day 1 Testing
Date | Start Time (EST) | Stop Time (EST) | GEMINI Operator Name | Facility Operator Name | Filename | Converted Filename | ACTIONS / STATUS | Test Objective | Count Rate (Hz) | Counts (n) | Dwell Time (s) | Foil | North Deflector Voltage (V) | South Deflector Voltage (V) | Rotational Stage (Axis 2) (deg) | IS Pressure (Torr) | IT Pressure (Torr) | Focus 1 | Focus 2 | Emission current (mA) | Ext (%) | Px (mm) | Py (mm) | Wien Filter Plate Potential | Energy | Ion Source Energy & Species | Helmholtz Coil Voltage (V) | Helmholtz Coil Current (A) | Helmholtz Coil Status (On/Off) | BM Status | SC Gate Valve | MC Gate Valve | Science Chamber Pressure (Torr) | Main Chamber Pressure (Torr) | Beamline Gate Valve | Comments
2026-04-23 |  | 11:16:00 | WJL | JSR | FL01 | 260423_p_1000_0_N |  | First light data with "0" V on Deflector Plates | 7.7 | 231 | 30 | None | 39 | -37 | 0 |  |  | 800 | 0 |  | 92 | -4 | 1.75 | 157.5 | 1 keV | 1 keV p+ | 5.69 | 0.43 | On
2026-04-23 |  | 11:23:00 | WJL | JSR | FL02 | 260423_p_1000_250_N |  | First light data with +/- 250 V on Deflector Plates | 12.2 | 366 | 30 | None | 250 | -250 | 0 |  |  | 800 | 0 |  | 92 | -4 | 1.75 | 157.5 | 1 keV | 1 keV p+ | 5.69 | 0.43 | On
2026-04-23 |  | 11:26:00 | WJL | JSR | FL03 | 260423_p_1000_500_N |  | First light data with +/- 500 V on Deflector Plates | 41.27 | 1238 | 30 | None | 500 | -500 | 0 |  |  | 800 | 0 |  | 92 | -4 | 1.75 | 157.5 | 1 keV | 1 keV p+ | 5.69 | 0.43 | On
2026-04-23 |  | 11:31:00 | WJL | JSR | FL04 | 260423_p_1000_750_N |  | First light data with +/- 750 V on Deflector Plates | 65.97 | 1979 | 30 | None | 750 | -750 | 0 |  |  | 800 | 0 |  | 92 | -4 | 1.75 | 157.5 | 1 keV | 1 keV p+ | 5.69 | 0.43 | On
2026-04-23 |  | 11:33:00 | WJL | JSR | FL05 | 260423_p_1000_1084_N |  | First light data at target Deflector Plate Voltage +/- 1084 V | 88.07 | 2642 | 30 | None | 1084 | -1084 | 0 |  |  | 800 | 0 |  | 92 | -4 | 1.75 | 157.5 | 1 keV | 1 keV p+ | 5.69 | 0.43 | On
2026-04-23 |  |  | WJL | JSR | FL06 | 260423_p_1000_1084_C_BAD | Rotated rotational stage axis 2 to 54.12 degrees. Data got overwritten. See FL06 2 rows down |  | 102.87 Hz |  |  | 0.6 ug/cm^2 | 1084 | -1084 | 54.12 |  |  | 800 | 0 |  | 92 | -4 | 1.75 | 157.5 | 1 keV | 1 keV p+ | 5.69 | 0.43 | On
2026-04-23 |  | 11:44:00 | WJL | JSR | FL07 | 260423_p_1000_750_C | Ramped voltage down to 750 V in one step | Attempt to see angular scattering and charge state separation through carbon foil | 81 | 2430 | 30 | 0.6 ug/cm^2 | 750 | -750 | 54.12 |  |  | 800 | 0 |  | 92 | -4 | 1.75 | 157.5 | 1 keV | 1 keV p+ | 5.69 | 0.43 | On
2026-04-23 |  | 11:46:00 | WJL | JSR | FL06 | 260423_p_1000_1084_C | Ramped voltage up to 1084 in one step | Same as FL06 because it got overwritten. Deflector plates back at target voltages | 97.5 | 2925 | 30 | 0.6 ug/cm^2 | 1084 | -1084 | 54.12 |  |  | 800 | 0 |  | 92 | -4 | 1.75 | 157.5 | 1 keV | 1 keV p+ | 5.69 | 0.43 | On
2026-04-23 | 11:47:00 |  | WJL | JSR | FL08 | 260423_p_1000_500_C | Ramped voltage down to 500 V in 250V steps | Lowering Deflector Plate voltages to attempt to see charge state separation | 52.57 | 1577 | 30 | 0.6 ug/cm^2 | 500 | -500 | 54.12 |  |  | 800 | 0 |  | 92 | -4 | 1.75 | 157.5 | 1 keV | 1 keV p+ | 5.69 | 0.43 | On
2026-04-23 | 11:51:00 |  | WJL | JSR | FL09 | 260423_p_1000_750_C_2 | Ramped voltage up to 750 V in one step | Attempt to see charge state separation | 82.9 | 2487 | 30 | 0.6 ug/cm^2 | 750 | -750 | 54.12 |  |  | 800 | 0 |  | 92 | -4 | 1.75 | 157.5 | 1 keV | 1 keV p+ | 5.69 | 0.43 | On
2026-04-23 |  | 11:58:00 | WJL | JSR | FL10 | 260423_p_1000_1084_C_2 | Ramped voltage up to 1084 V in one step | Attempt to see charge state separation | 101.5 | 3045 | 30 | 0.6 ug/cm^2 | 1084 | -1084 | 54.12 |  |  | 800 | 0 |  | 92 | -4 | 1.75 | 157.5 | 1 keV | 1 keV p+ | 5.69 | 0.43 | On
2026-04-23 | 11:58:00 |  | WJL | JSR | FL11 | 260423_p_1000_1084_G | Moved rotational stage Axis 2 from 54.12deg to neg 54.12 deg | Put ion beam on graphene foil for the first time! | 103.8 | 3114 | 30 | Graphene | 1084 | -1084 | -54.12 |  |  | 800 | 0 |  | 92 | -4 | 1.75 | 157.5 | 1 keV | 1 keV p+ | 5.69 | 0.43 | On
2026-04-23 | 12:03:00 |  | WJL | JSR | FL12 | 260423_p_1000_0_G | Ramped down voltages from 1084 V to 0 V in 250 V steps | See difference between deflector plates on and off in trying to make a stripe | 5.93 | 178 | 30 | Graphene | 40 | -31 | -54.12 |  |  | 800 | 0 |  | 92 | -4 | 1.75 | 157.5 | 1 keV | 1 keV p+ | 5.69 | 0.43 | On |  |  |  |  |  | Open
2026-04-23 | 12:17:00 |  | WJL | JSR | DC02 | 260423_p_0_0_G_CLOSED | Rotated rotational stage back to home and closed the Beamline GV. There is some artifact at 6 o'clock on the MCP. Ion gauge? | Take a dark counts baseline | 7.42 | 2226 | 300 | None | 40 | -31 | 0 |  |  | 800 | 0 |  | 92 | -4 | 1.75 | 157.5 | 1 keV | 1 keV p+ | 5.69 | 0.43 | On |  |  |  |  |  | Closed
2026-04-23 |  |  | WJL | JSR | DC03 | 260423_p_0_0_G_CLOSED_2 | Turned off Science Chamber ion gauge | Take a real dark counts baseline without ion gauge | 0.94 | 283 | 300 | None | 40 | -31 | 0 |  |  | 800 | 0 |  | 92 | -4 | 1.75 | 157.5 | 1 keV | 1 keV p+ | 5.69 | 0.43 | On |  |  |  |  |  | Closed
2026-04-23 | 12:26:00 |  | WJL | LYK? | FC14 | 260423_p_1000_1084_C_3 | Rotated to carbon foil, ramped up deflector plate voltages in 250V increments, opened Beamline GV | Attempting to see charge separation through carbn | 1.27 | 380 | 300 | 0.6 ug/cm^2 | 1084 | -1084 | 54.12 | 1E-7 Torr |  | 800 | 0 |  | 92 | -4 | 1.75 | 157.5 | 1 keV | 1 keV p+ | 5.69 | 0.43 | On |  |  |  |  |  | Open
2026-04-23 |  |  | WJL | LYK | FL15 | 260423_p_1000_1084_N_2 | Increasing IS Pressure to 1E-6 Torr. Opening beamline GV. Returned rotational stage to home (no foil) 48 Hz? It looks like there is a neutral and ion component to the beam | Baseline for 1E-6 Torr on no-foil so we know how much we can increase the p-leadk by to get better statistics | 4.28 | 583 | 120 | None | 1084 | -1084 | 0 | 1E-6 Torr |  | 800 | 0 |  | 92 | -4 | 1.75 | 157.5 | 1 keV | 1 keV p+ | 5.69 | 0.43 | On
2026-04-23 |  |  | WJL | LYK | FL16 | 260423_p_0_0_N | Ramped down deflector plates to 0 V in 250 V increments. Same as FL15 with exception of those deflector plates | Do we still see the little dot? Yes. Yes we do | 4.69 | 589 | 125.5 | None | 39 | -29 | 0 | 1E-6 Torr |  | 800 | 0 |  | 92 | -4 | 1.75 | 157.5 | 1 keV | 1 keV p+ | 5.69 | 0.43 | On
2026-04-23 |  |  | WJL | LYK | FL17 |  |  | See count rate through the carbon foil as we increase IS pressure | 1.99 |  | 120 | 0.6 ug/cm^2 | 1084 | -1084 | 54.12 | 5E-6 Torr |  | 800 | 0 |  | 92 | -4 | 1.75 | 157.5 | 1 keV | 1 keV p+ | 5.69 | 0.43 | On
2026-04-23 |  |  | WJL | LYK | FL18 |  |  | Increasing IS Pressure while staying on carbon foil | 2.97 |  |  | 0.6 ug/cm^2 | 1084 | -1084 | 54.12 | 1.0E-5 Torr |  | 800 | 0 |  | 92 | -4 | 1.75 | 157.5 | 1 keV | 1 keV p+ | 5.69 | 0.43 | On
2026-04-23 |  |  | WJL | LYK | FL19 |  |  | Further increasing IS pressure while staying on carbon foil | 4.77 |  |  | 0.6 ug/cm^2 | 1084 | -1084 | 54.12 | 2.0E-5 Torr |  | 800 | 0 |  | 92 | -4 | 1.75 | 157.5 | 1 keV | 1 keV p+ | 5.69 | 0.43 | On
2026-04-23 | 15:10:00 |  | WJL | JSR | FL20 |  | Turned ion gauge off after returning from lunch. MCP back up to 1800 V. Current 0.902 mA. Confirmed carbon foil is in the beam when we open the beamline GV | Finding the charge state separation at lower deflector plate energies | 6.11 | 733 | 120 | 0.6 ug/cm^2 | 750 | -750 | 54.12 | 1.75E-5 Torr |  | 800 | 0 |  | 92 | -4 | 1.75 | 157.5 | 1 keV | 1 keV p+ | 5.69 | 0.43 | On |  | Open | Open |  |  | Open
2026-04-23 |  |  | WJL | JSR | FL21 |  | We still don't see 3 separate stripes hmm…. | Finding the charge state separation at lower deflector plate energies | 6.44 |  |  | 0.6 ug/cm^2 | 500 | -500 | 54.12 | 1.7E-5 Torr |  | 800 | 0 |  | 92 | -4 | 1.75 | 157.5 | 1 keV | 1 keV p+ | 5.69 | 0.43 | On
2026-04-23 |  |  | WJL | JSR | FL22 |  | Still not seeing any movement of the stripe. | Trying to decide if we're seeing 1 stripe or 3 overlapping stripes | 5.97 |  |  | 0.6 ug/cm^2 | 250 | -250 | 54.12 |  |  | 800 | 0 |  | 92 | -4 | 1.75 | 157.5 | 1 keV | 1 keV p+ | 5.69 | 0.43 | On
2026-04-23 |  |  | WJL | JSR | FL23 |  | Still not seeing any movement of the stripes! | Basically turning deflector plates off to see the stripe without any charge state separation | 5.81 | 697 |  | 0.6 ug/cm^2 | 39 | -28 | 54.12 |  |  | 800 | 0 |  | 92 | -4 | 1.75 | 157.5 | 1 keV | 1 keV p+ | 5.69 | 0.43 | On
2026-04-23 |  |  | WJL | JSR | FL24 |  | Still not seeing any movement! | Increasing the deflector plate voltages to try to induce angular separation | 6.19 | 743 |  | 0.6 ug/cm^2 | 1250 | -1250 | 54.12 |  |  | 800 | 0 |  | 92 | -4 | 1.75 | 157.5 | 1 keV | 1 keV p+ | 5.69 | 0.43 | On
2026-04-23 |  |  | WJL | JSR | FL25 |  |  | Increasing the deflector plate voltages again to try to induce angular separation |  |  |  | 0.6 ug/cm^2 | 2000 | -2000 | 54.12 |  |  | 800 | 0 |  | 92 | -4 | 1.75 | 157.5 | 1 keV | 1 keV p+ | 5.69 | 0.43 | On
2026-04-23 |  |  | WJL | JSR | FL26 |  | Turned off the Helmholtz coil to see if we're seeing the neutral background. Conclusion: The stripe is definitely caused by the ION beam hitting the foil because with HC off we no longer see a stripe | See if we are just seeing the neutral background | 2.48 | 298 |  | 0.6 ug/cm^2 | 2000 | -2000 | 54.12 |  |  | 800 | 0 |  | 92 | -4 | 1.75 | 157.5 | 1 keV | 1 keV p+ | 0 | 0 | Off
2026-04-23 |  |  | WJL | JSR | FL27 |  | Moving over to graphene foil. Helmholtz coil back on. There are no more stripes… Very quiet MCP | Determine angular scattering at target voltage on deflector plates. Through graphene! | 1.69 | 203 |  | Graphene | 1084 | -1084 | -54.12 | 1E-5 Torr |  | 800 | 0 |  | 92 | -4 | 1.75 | 157.5 | 1 keV | 1 keV p+ | 5.69 | 0.43 | On
2026-04-23 |  |  | WJL | JSR | FL28 |  | Still not seeing anything at all. | Reducing voltage on deflector plates to bring the ions back? | 1.58 | 198 |  | Graphene | 750 | -750 | -54.12 | 1E-5 Torr |  | 800 | 0 |  | 92 | -4 | 1.75 | 157.5 | 1 keV | 1 keV p+ | 5.69 | 0.43 | On
2026-04-23 |  |  | WJL | JSR | FL29 |  | Absolutely nothing. Maybe the graphene is blocking and not letting anything through?? | Zero deflector plate voltage to see if anything gets through the graphene at all | 1.29 |  |  | Graphene | 38 | -27 | -54.12 |  |  | 800 | 0 |  | 92 | -4 | 1.75 | 157.5 | 1 keV | 1 keV p+ | 5.69 | 0.43 | On
2026-04-23 |  |  | WJL | JSR | FL30 |  | Increased beam energy to 4 keV proton. Ready to close beamline GV if needed. | Trying to punch through the graphene with a higher energy beam since we're not seeing anything | 1.18 |  |  | Graphene | 39 | -28 | -54.12 |  |  | 3200 | 0 |  | 95 | -4 | 1.75 | 315 | 4 keV | 4 keV p+ | 5.69 | 0.43 | On
2026-04-23 |  |  | WJL | JSR | FL31 |  | 4 keV protons on carbon to see if we fried the MCP… We did not! We see an elliptical distribution!!! Lower angular scattering with higher beam energy as expected! | Returning to carbon where we know what the output is supposed to look like. Verifying that we didn't fry the MCP. Expecting to see a stripe on the MCP | 20.6 |  |  | 0.6 ug/cm^2 | 39 | -28 | 54.12 |  |  | 3200 | 0 |  | 95 | -4 | 1.75 | 315 | 4 keV | 4 keV p+ | 5.69 | 0.43 | On
2026-04-23 |  |  | WJL | JSR | FL32 |  | 1 keV proton on carbon with no deflector voltages just to reestablish our results from earlier | Returning to 1 keV proton on carbon with no deflector voltages to reestablish our results from earlier | 5.68 | 682 |  | 0.6 ug/cm^2 | 39 | -28 | 54.12 |  |  | 800 | 0 |  | 92 | -4 | 1.75 | 157.5 | 1 keV | 1 keV p+ | 5.69 | 0.43 | On
2026-04-23 |  |  | WJL | JSR | FL33 |  | Changed p-leak so that the IS Pressure is 7.3E-7 Torr. We see the dot as expected | Sanity check to make sure the deflector plates still work. Starting at "0"V on the deflectors and will ramp up in the next test | 10.51 |  |  | None | 39 | -28 | 0 | 7.3E-7 Torr |  | 800 | 0 |  | 92 | -4 | 1.75 | 157.5 | 1 keV | 1 keV p+ | 5.69 | 0.43 | On
2026-04-23 |  |  | WJL | JSR | FL34 |  | Ramped voltages back up to +/- 1084 V, we see the dot moves! Maybe we get some neutral scattering from the interaction with the nickel grid? The deflectors are still working! | Verifying that the deflector plates still work. | 8.5 |  |  | None | 1084 | -1084 | 0 |  |  | 800 | 0 |  | 92 | -4 | 1.75 | 157.5 | 1 keV | 1 keV p+ | 5.69 | 0.43 | On
2026-04-23 |  |  | WJL | JSR | FL35 |  | The dot moves closer to the middle as expected! | Moving the dot further away from the edge to see if the central dot is caused by scattering | 8.61 |  |  | None | 750 | -750 | 0 | 5E-7 Torr |  | 800 | 0 |  | 92 | -4 | 1.75 | 157.5 | 1 keV | 1 keV p+ | 5.69 | 0.43 | On

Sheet: Day 2 Testing
Date | Start Time (EST) | Stop Time (EST) | GEMINI Operator Name | Facility Operator Name | Filename | Converted Filename | ACTIONS / STATUS | Test Objective | Count Rate (Hz) | Counts (n) | Dwell Time (s) | Foil | North Deflector Voltage (V) | South Deflector Voltage (V) | Rotational Stage (Axis 2) (deg) | IS Pressure (Torr) | IT Pressure (Torr) | Focus 1 | Focus 2 | Emission current (mA) | Ext (%) | Px (mm) | Py (mm) | Wien Filter Plate Potential | Energy | Ion Source Energy & Species | Helmholtz Coil Voltage (V) | Helmholtz Coil Current (A) | Helmholtz Coil Status (On/Off) | BM Status | SC Gate Valve | MC Gate Valve | Science Chamber Pressure (Torr) | Main Chamber Pressure (Torr) | Beamline Gate Valve | Comments
2026-04-24 | 9:15:00 | 9:20:00 | WJL | LYK | DC04 |  | Turned SC ion gauge off, closed Beamline GV, MCP at 1800 V | Dark counts test to get the background rate before we start the day | 1.09 | 328 | 300 | None | 0 | 0 | 0 | 1e-06 |  | 800 | 0 |  | 92 | -4 | 1.75 | 157.5 | 1 keV | 1 keV p+ | 5.67 | 0.43 | On | Off | Open | Open |  | 3.2e-08 | Closed
 |  |  | WJL | LYK | E01 |  | Seeing a stripe but a lot less defined than yesterday because the IS pressure is lower | Baseline for beam through carbon foil without deflector plates on | 1.89 |  | 120 | Carbon | 0 | 0 | 54.12 | 1e-06 |  | 800 | 0 |  | 92 | -4 | 1.75 | 157.5 | 1 keV | 1 keV p+ | 5.67 | 0.43 | On |  | Open | Open |  |  | Open
 |  |  | WJL | LYK | E02 |  | Maybee a stripe on the left face | Turning north deflector plate on to separate electrons | 2.07 |  | 120 | Carbon | 5.01 | 0 | 54.12 | 1e-06 |  | 800 | 0 |  | 92 | -4 | 1.75 | 157.5 | 1 keV | 1 keV p+ | 5.67 | 0.43 | On |  | Open | Open |  |  | Open
 |  |  | WJL | LYK | E03 |  | Closed beamline GV before increasing IS pressure to 1E-5 Torr to get more counts | Increasing IS pressure with same parameters as E02 to get a more defined electron emission line | 3.95 |  | 120 | Carbon | 5.01 | 0 | 54.12 | 1.1e-05 |  | 800 | 0 |  | 92 | -4 | 1.75 | 157.5 | 1 keV | 1 keV p+ | 5.67 | 0.43 | On |  | Open | Open |  |  | Open
 |  |  | WJL | LYK | E04 |  | Increased deflector plate voltage to 6.01 V | Increasing deflector plate voltage to separate out secondary electrons | 4.39 |  | 120 | Carbon | 6.01 | 0 | 54.12 | 1.1e-05 |  | 800 | 0 |  | 92 | -4 | 1.75 | 157.5 | 1 keV | 1 keV p+ | 5.67 | 0.43 | On |  | Open | Open |  |  | Open
 |  |  | WJL | LYK | E05 |  | Increased IS pressure to 2E-5 Torr because right now the highest pixel is 5 Hz so we might not be able to distinguish electrons from background counts. We think we might see a group of electrons! Not a stripe but could be due to asymmetry in the instrument. | Binary search to find where the secondary electron stripe is | 6.52 |  | 120 | Carbon | 6.01 | 0 | 54.12 | 2e-05 |  | 800 | 0 |  | 92 | -4 | 1.75 | 157.5 | 1 keV | 1 keV p+ | 5.67 | 0.43 | On |  | Open | Open |  |  | Open
 | 9:51:00 |  | WJL | LYK | E06 |  | We no longer see the cluster of maybe electrons!! Did we sweep it off the MCP by increasing the deflector plate voltage? Maybe. The count rate went down though | Binary search to find where the secondary electron stripe is | 6.75 |  | 120 | Carbon | 10.01 | 0 | 54.12 | 2e-05 |  | 800 | 0 |  | 92 | -4 | 1.75 | 157.5 | 1 keV | 1 keV p+ | 5.67 | 0.43 | On |  | Open | Open |  |  | Open
 | 9:54:00 |  | WJL | LYK | E07 |  | We do not see the cluster | Reducing deflector plate voltage to see if we bring back the (potential) secondary electron cluster | 7.34 |  | 120 | Carbon | 8.01 | 0 | 54.12 | 2e-05 |  | 800 | 0 |  | 92 | -4 | 1.75 | 157.5 | 1 keV | 1 keV p+ | 5.67 | 0.43 | On |  | Open | Open |  |  | Open
 | 9:58:00 |  | WJL | LYK | E08 |  | We do not see the cluster | Reducing deflector plate voltage again to try to bring back the secondary electrons | 6.78 |  | 120 | Carbon | 7 | 0 | 54.12 | 2e-05 |  | 800 | 0 |  | 92 | -4 | 1.75 | 157.5 | 1 keV | 1 keV p+ | 5.67 | 0.43 | On |  | Open | Open |  |  | Open
 | 10:01:00 |  | WJL | LYK | E09 |  | No cluster | Reducing deflector plate voltage in finer steps to try to bring back the secondary electrons | 7.42 |  | 120 | Carbon | 6.51 | 0 | 54.12 | 2e-05 |  | 800 | 0 |  | 92 | -4 | 1.75 | 157.5 | 1 keV | 1 keV p+ | 5.67 | 0.43 | On |  | Open | Open |  |  | Open
 | 10:03:00 |  | WJL | LYK | E10 |  | There was a small cluster maybe but probably just statistics and not in the same x position as before | Returning to 6 V to see if the cluster was just statistics :( | 7.05 |  | 120 | Carbon | 6.01 | 0 | 54.12 | 2e-05 |  | 800 | 0 |  | 92 | -4 | 1.75 | 157.5 | 1 keV | 1 keV p+ | 5.67 | 0.43 | On |  | Open | Open |  | 3.4e-08 | Open
 | 10:07:00 |  | WJL | LYK | E11 |  | Just a stripe | Reducing deflector plate voltage even further to try to see the secondary electrons | 7.42 |  | 120 | Carbon | 5.01 | 0 | 54.12 | 2e-05 |  | 800 | 0 |  | 92 | -4 | 1.75 | 157.5 | 1 keV | 1 keV p+ | 5.67 | 0.43 | On |  | Open | Open |  | 3.4e-08 | Open
 | 10:10:00 |  | WJL | LYK | E12 |  | Just a stripe | Reducing deflector plate voltage further to try to see secondary electrons | 7.77 |  | 120 | Carbon | 4.01 | 0 | 54.12 |  |  |  |  |  |  |  |  |  |  |  | 5.67 | 0.43 | On
 | 10:12:00 |  | WJL | LYK | E13 |  | Just a stripe | Ramping deflector plate voltage down to see if we see anything interesting | 7.1 |  | 120 | Carbon | 3.01 | 0 | 54.12 |  |  |  |  |  |  |  |  |  |  |  | 5.67 | 0.43 | On
 | 10:15:00 |  | WJL | LYK | E14 |  | Just a stripe | Ramping deflector plate voltage down to see if we see anything interesting | 7.68 |  | 120 | Carbon | 2.01 | 0 | 54.12 |  |  |  |  |  |  |  |  |  |  |  | 5.67 | 0.43 | On
 | 10:17:00 |  | WJL | LYK | E15 |  |  | Ramping deflector plate voltage down to see if we see anything interesting | 8.07 |  | 120 | Carbon | 1 | 0 | 54.12 |  |  |  |  |  |  |  |  |  |  |  | 5.67 | 0.43 | On
 | 10:20:00 |  | WJL | LYK | E16 |  |  | Ramping deflector plate voltage down to see if we see anything interesting | 7.72 |  | 120 | Carbon | 0 | 0 | 54.12 |  |  |  |  |  |  |  |  |  |  |  | 5.67 | 0.43 | On
 | 10:25:00 |  | WJL | LYK | E17 |  | Closed beamline GV before rotrating to graphene, set deflector plate voltage to 4 V. Do not see anything. Looks just like random noise | Searching for secondary electron emission from graphene | 2.27 |  | 120 | Graphene | 4 | 0 | -54.12 | 1.9e-05 |  |  |  |  |  |  |  |  |  |  | 5.67 | 0.43 | On
 | 10:28:00 |  | WJL | LYK | E18 |  | Maybeee there is a little cluster? But graphene has low secondary electron yield | Searching for secondary electron emission from graphene | 2.62 |  | 120 | Graphene | 5.01 | 0 | -54.12 | 1.9e-05 |  |  |  |  |  |  |  |  |  |  | 5.67 | 0.43 | On
 | 10:30:00 |  | WJL | LYK | E19 |  |  | Still searching for secondary electron emission from graphene | 2.37 |  | 120 | Graphene | 6 | 0 | -54.12 | 1.9e-05 |  |  |  |  |  |  |  |  |  |  | 5.67 | 0.43 | On
 | 10:36:00 |  | WJL | LYK | E20 |  | Increased beam energy to 4 keV and also bumped the IS pressure a litle bit because it has been pumping down | Searching for secondary electron emission from grapheneat a higher beam energy | 3.63 |  | 120 | Graphene | 6 | 0 | -54.12 | 2.3e-05 |  |  |  |  |  |  |  |  | 4 keV | 4 keV p+ | 5.67 | 0.43 | On
 | 10:38:00 |  | WJL | LYK | E21 |  | Still nothing | Searching for secondary electron emission from grapheneat a higher beam energy | 3.52 |  | 120 | Graphene | 5.01 | 0 | -54.12 | 2.3e-05 |  |  |  |  |  |  |  |  |  |  |  |  | On
 | 10:41:00 |  | WJL | LYK | E22 |  | Still seeing nothing | Searching for secondary electron emission from grapheneat a higher beam energy | 3.57 |  | 120 | Graphene | 4.01 | 0 | -54.12 | 2.3e-05 |  |  |  |  |  |  |  |  |  |  |  |  | On
 |  |  | WJL | LYK | E23 |  | Closed beamline GV and moved foil to carbon in front of the beam. Then opened beamline GV | Searching for secondary electron emission from graphene through amorphous carbon | 30.07 |  | 120 | Carbon | 4 | 0 | 54.12 | 2.3e-05 |  |  |  |  |  |  |  |  |  |  |  |  | On
 | 10:52:00 |  | WJL | LYK | E24 |  | We are getting about 30 Hz now in the core of the ellipse so we expect 3 Hz (10%) in the secondary electron stripe (which we are still not seeing) | Searching for secondary electron emission from graphene | 30.14 |  | 120 | Carbon | 5.01 | 0 | 54.12 | 2.3e-05 |  |  |  |  |  |  |  |  |  |  |  |  | On
 | 10:56:00 |  | WJL | LYK | E25 |  | Still no separation | Still searching for secondary electron emission from graphene | 30.96 |  | 120 | Carbon | 6.01 | 0 |  |  |  |  |  |  |  |  |  |  |  |  |  |  | On
 | 11:03:00 |  | WJL | LYK | E26 |  | Still no separation | Upping the deflector plate voltage. Maybe the secondary electrons are higher energy? | 29.63 |  | 120 | Carbon | 10.01 | 0 |  |  |  |  |  |  |  |  |  |  |  |  |  |  | On
 | 11:10:00 |  | WJL | LYK | S01 |  | Ok we are switching test campaigns now. We will keep the 4 keV p+ beam but now attempt to steer the charge state populations with better statistics. The charge state separation works! | HVPS on North and South at 3000 V!!! | 31.36 |  | 120 | Carbon | 3000 | -3000 | 54.12 | 2.2e-05 |  |  |  |  |  |  |  |  |  |  |  |  | On
 |  |  | WJL | LYK | S02 |  | Increased deflector plate voltage even more to 3500 V! | Prove that increasing deflector plate voltage increases steering gap | 31.64 |  | 120 | Carbon | 3500 | -3500 | 54.12 | 2.2e-05 |  |  |  |  |  |  |  |  |  |  |  |  | On
 | 11:18:00 |  | WJL | LYK | S03 |  | Decrease deflector plate voltages to 2500 V | Decrease deflector plate voltages to 2500 V to prove reducing steering gap | 31.86 |  | 120 | Carbon | 2500 | -2500 | 54.12 | 2.2e-05 |  |  |  |  |  |  |  |  |  |  |  |  | On
 | 11:20:00 |  | WJL | LYK | S04 |  | Dwelling for 5 minutes to get good statistics |  | 31.34 |  | 300 | Carbon | 3000 | -3000 | 54.12 | 2.2e-05 |  |  |  |  |  |  |  |  |  |  |  |  | On
 |  |  |  |  | G01 |  | Turning on Matsusada to float the beam up to 16 keV. Going up in 1 keV steps. Hypothesis to see what the stopping power of graphene is. Actual beamline voltage |  |  |  |  |  |  |  | -54.12 |  |  |  |  |  |  |  |  |  | 16 keV |  |  |  | On
 |  |  |  |  |  |  |  |  |  |  |  |  |  |  |  |  |  |  |  |  |  |  |  |  |  |  |  |  | On
 |  |  |  |  |  |  |  |  |  |  |  |  |  |  |  |  |  |  |  |  |  |  |  |  |  |  |  |  | On
 |  |  |  |  |  |  |  |  |  |  |  |  |  |  |  |  |  |  |  |  |  |  |  |  |  |  |  |  | On
 |  |  |  |  |  |  |  |  |  |  |  |  |  |  |  |  |  |  |  |  |  |  |  |  |  |  |  |  | On
 |  |  |  |  |  |  |  |  |  |  |  |  |  |  |  |  |  |  |  |  |  |  |  |  |  |  |  |  | On
 |  |  |  |  |  |  |  |  |  |  |  |  |  |  |  |  |  |  |  |  |  |  |  |  |  |  |  |  | On
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

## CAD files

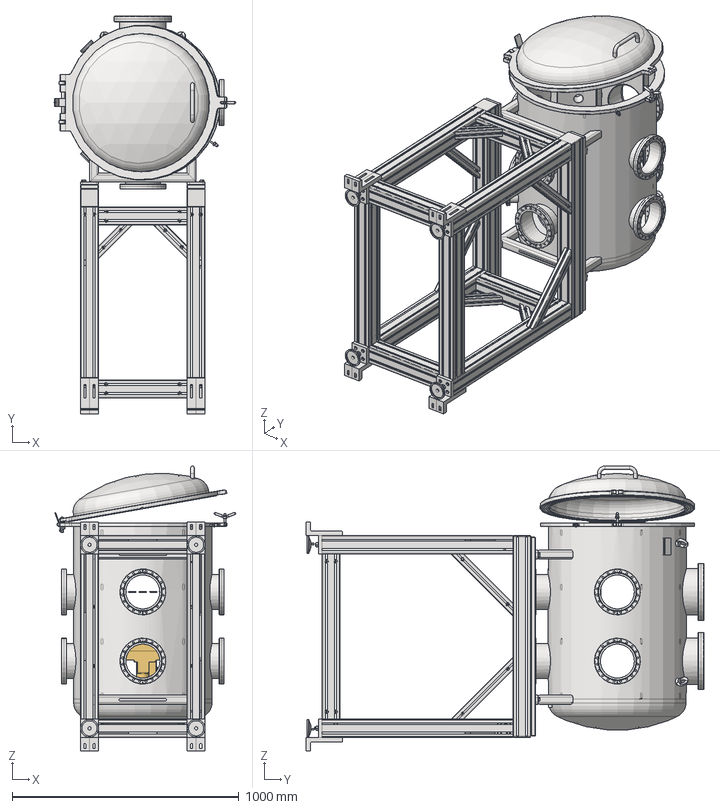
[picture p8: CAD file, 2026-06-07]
GEMINI-Documents/GEMINI-DownloadedCAD/SciChamberAssembly.stp
800.5 x 1752.6 x 1256.3 mm
TR-8880-00706
Bottom_Plate
mtn200ppv6
Linear_to_Rotational_Cone
rv120pe
NorCalScienceChamberDoor

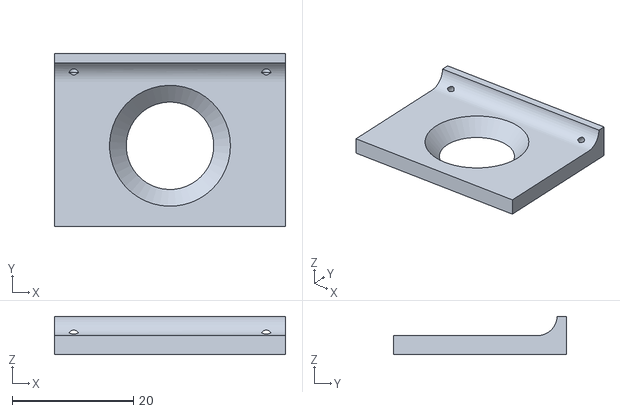
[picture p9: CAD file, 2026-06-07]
GEMINI-JP_3DPrints260128/APERTURE_PLATE_FULL.STL
38.1 x 28.6 x 6.35

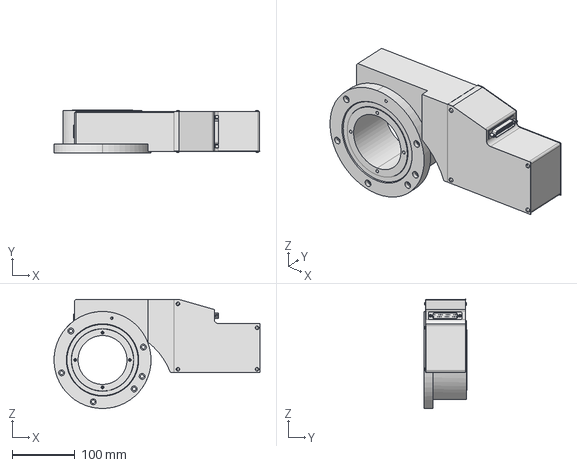
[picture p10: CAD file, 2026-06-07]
GEMINI-Documents/GEMINI-DownloadedCAD/Newport-RV120PE.stp
329.0 x 68.0 x 174.1 mm

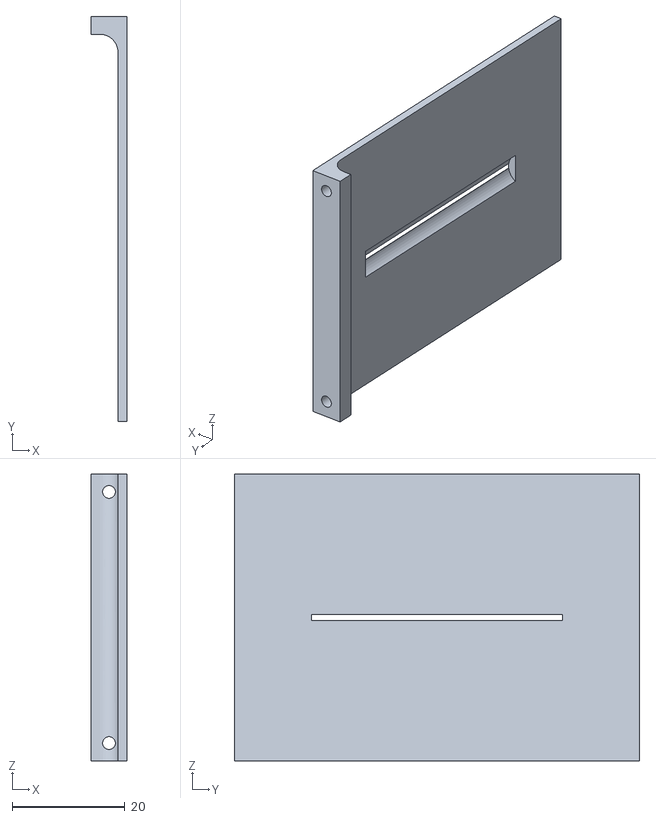
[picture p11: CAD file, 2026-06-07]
GEMINI-JP_3DPrints260128/SLIT_PLATE_FINAL.STL
6.35 x 71.7 x 50.8

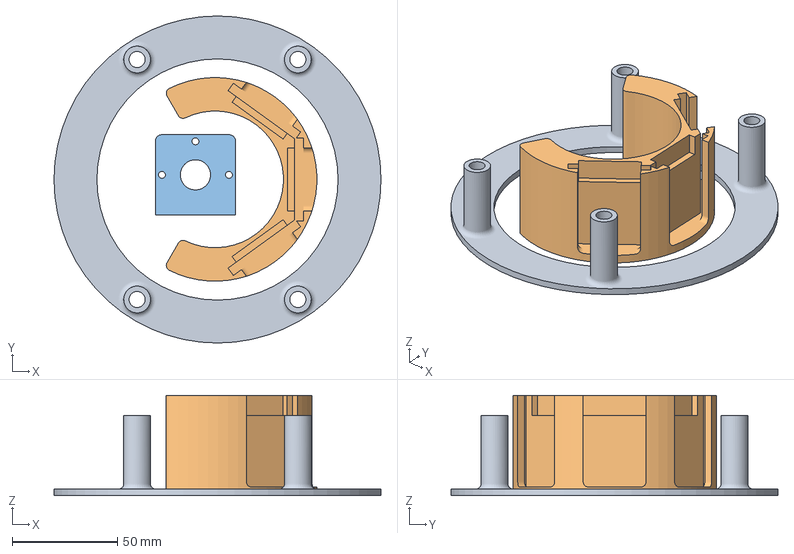
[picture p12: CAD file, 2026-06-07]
GEMINI-Solidworks/GSE/GEMINI_GSE.3mf
155.0 x 155.0 x 47.6 mm
OUTER_SKIRT_GSE.STL
INNER_SKIRT_GSE.STL
ABM_GRID_GSE.STL

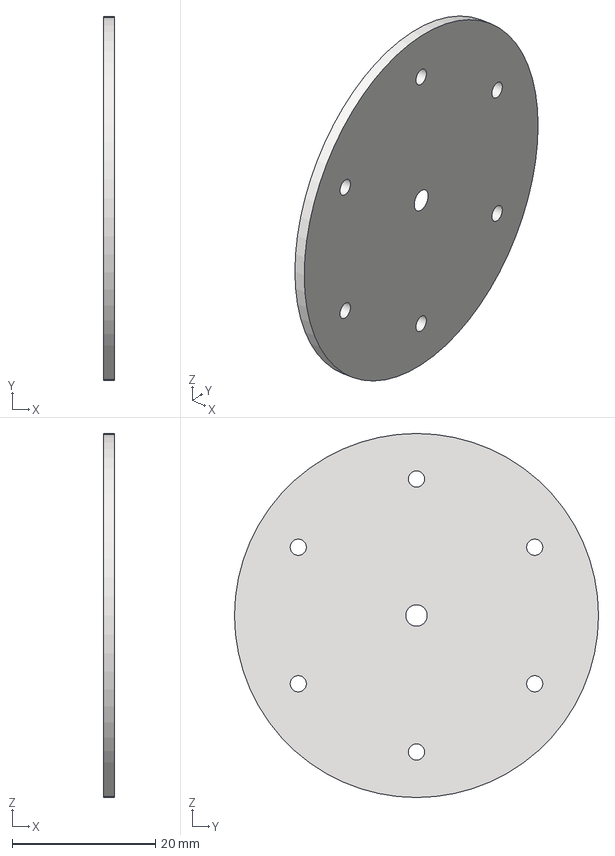
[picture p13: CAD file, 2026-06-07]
GEMINI-Documents/GEMINI-DownloadedCAD/3mmKnifeEdgeDisk.stp
1.59 x 50.8 x 50.8 mm

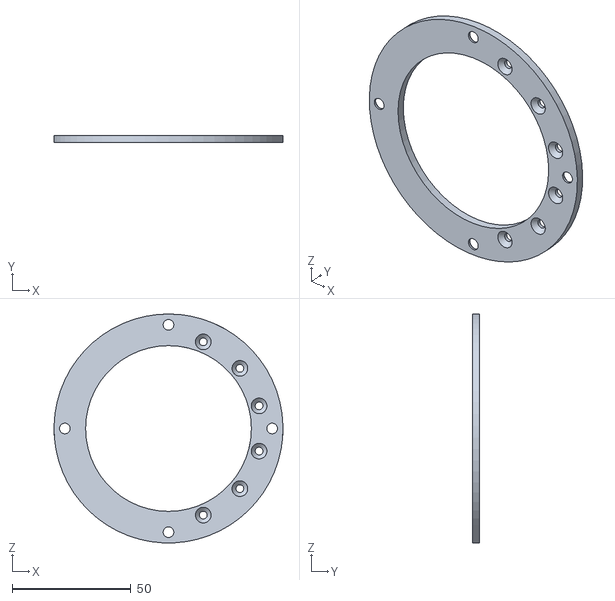
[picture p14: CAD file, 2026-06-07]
GEMINI-JP_3DPrints260128/INNER_SKIRT.STL
96.5 x 3.15 x 96.5

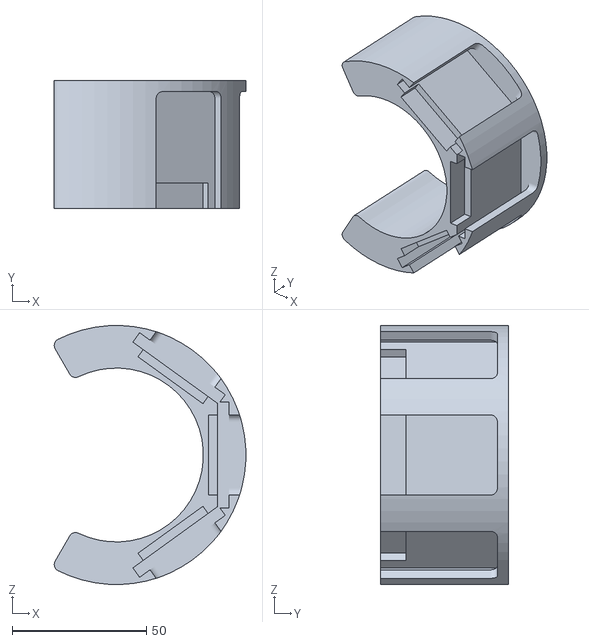
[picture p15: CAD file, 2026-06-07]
GEMINI-Solidworks/GSE/INNER_SKIRT_GSE.STL
71.4 x 47.6 x 96.5

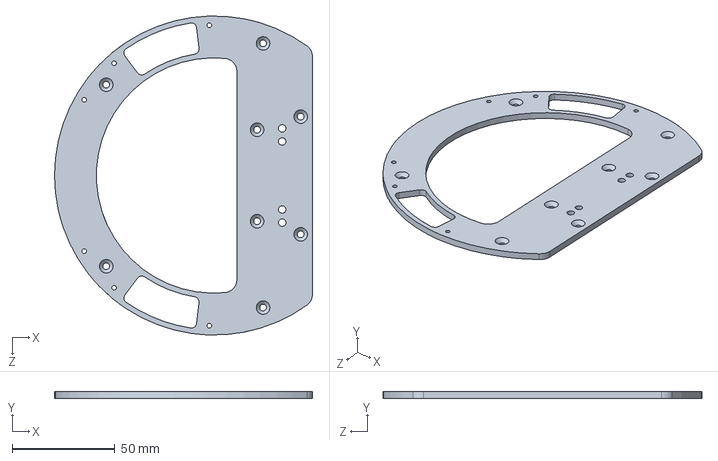
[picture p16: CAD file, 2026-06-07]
GEMINI-Solidworks/ROOF.SLDPRT
125.3 x 3.17 x 154.9 mm

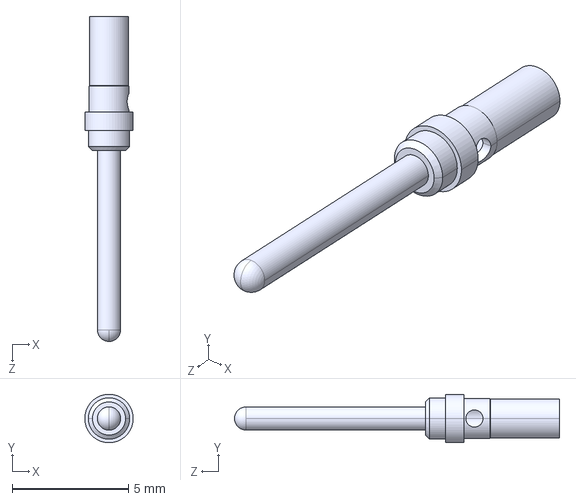
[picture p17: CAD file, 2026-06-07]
GEMINI-Documents/GEMINI-DownloadedCAD/MC6020D.stp
2.08 x 2.08 x 14.0 mm

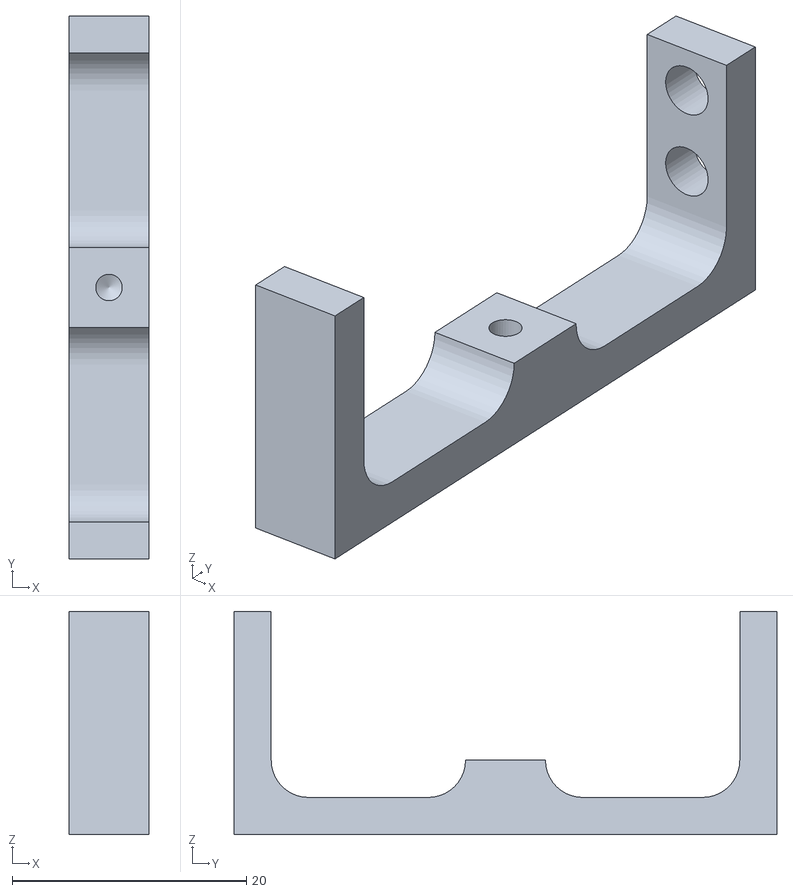
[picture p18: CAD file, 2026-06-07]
GEMINI-JP_3DPrints260128/DEFLECTOR_PLATE_NORTH.STL
6.82 x 46.3 x 19.0

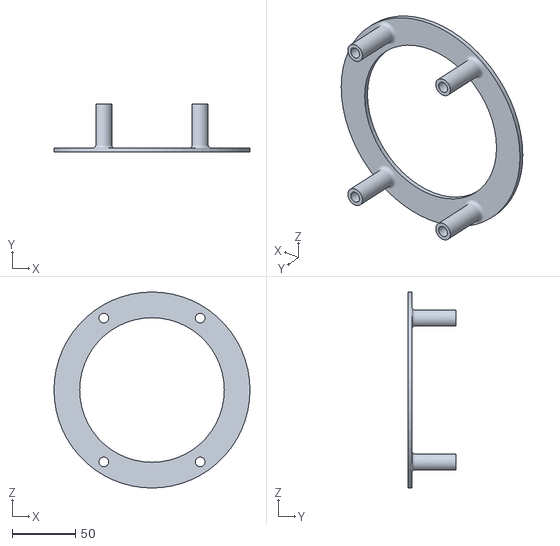
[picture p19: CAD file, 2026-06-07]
GEMINI-Solidworks/GSE/OUTER_SKIRT_GSE.STL
155.0 x 38.1 x 155.0

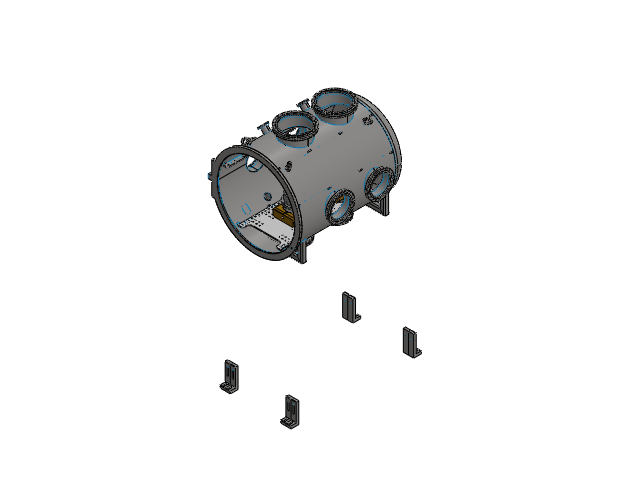
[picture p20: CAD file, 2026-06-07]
GEMINI-Solidworks/SciChamberAssemblyGEMINI.SLDASM
TR-8880-00706
Bottom_Plate
mtn200ppv6
Linear_to_Rotational_Cone
rv120pe

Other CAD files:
GEMINI-Solidworks/Cable_1-GEMINI-00-00-00.SLDASM
GEMINI-Solidworks/SciChamberAssembly.stp
GEMINI-Solidworks/DUMMY_M3_PARTS.SLDASM
GEMINI-Solidworks/Cable_2-GEMINI-00-00-00.SLDASM
GEMINI-Solidworks/GEMINI-00-00-00-L.SLDPRT
GEMINI-Documents/GEMINI-DownloadedCAD/FC6020D2_AA.stp
GEMINI-Documents/GEMINI-DownloadedCAD/Newport-RV120PE.3mf
GEMINI-Documents/GEMINI-DownloadedCAD/mcp_3394.stp
GEMINI-JP_3DPrints260128/ABM_GRID.3mf
GEMINI-JP_3DPrints260128/ABM_GRID.STL
GEMINI-JP_3DPrints260128/APERTURE_PLATE_PINHOLE.STL
GEMINI-JP_3DPrints260128/APERTURE_ROTATION_PLATE_1.STL
GEMINI-JP_3DPrints260128/APERTURE_ROTATION_PLATE_FINAL.STL
GEMINI-JP_3DPrints260128/DEFLECTOR_PLATE_SOUTH.STL
GEMINI-JP_3DPrints260128/DUMMY_M3_SPACER.3mf
GEMINI-JP_3DPrints260128/DUMMY_M3_SPACER.STL
GEMINI-JP_3DPrints260128/GRID_HOLDER.STL
GEMINI-JP_3DPrints260128/MCP_MOUNTING_BRACKET.STL
GEMINI-JP_3DPrints260128/ROOF.3mf
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

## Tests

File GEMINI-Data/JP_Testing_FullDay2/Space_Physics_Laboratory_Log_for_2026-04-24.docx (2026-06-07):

# Space Physics Laboratory Logbook Princeton University - 171 Broadmead

April 24, 2026 (Friday)

08:00 – LYK

Open the lab with William. We are going to do RGA scan and the ion source ignition.

08:45 – LYK

Completed the RGA scan for science chamber. The overall trend is better but there is still a spike near 102 (likely sapphire related).

09:09 – LYK

Change the IS beam to 1keV proton at IS = 1E-6 Torr. MCP is now at 1400 V. Open the SC GF and Beamline GV. Going to slowly ramp up MCP to 1800 V.

09:13 – LYK

We saw about 30 Hz in the ‘baseline’ mode, i.e., open aperture. Close the beamline GV.

Turn off the SC ion gauge to do dark count test.

The plan for today is as follows:

1) Dark count test
2) Carbon Foil
  a. Electron yield test with 1 keV p+
3) Move to Graphene
  a. Electron yield test with 1keV p+
4) Change the beam to 4keV p+
5) Move to Carbon Foil
  a. Electron yield test with 4keV p+
6) Graphene
  a. Electron yield test with 4keV p+
7) Repeat the scattering test with 4keV p+

09:24 – LYK

IS pressure drops during the dark count test, so adjust it back from 8E-7 Torr to 1E-6 Torr

09:37 – LYK
Close the BL GV to change the IS pressure from 1E-6 to 1E-5 Torr because the count rates are too low (~2.07 Hz) when in electron yield test.

This is what we see with 5 V on deflector plate….

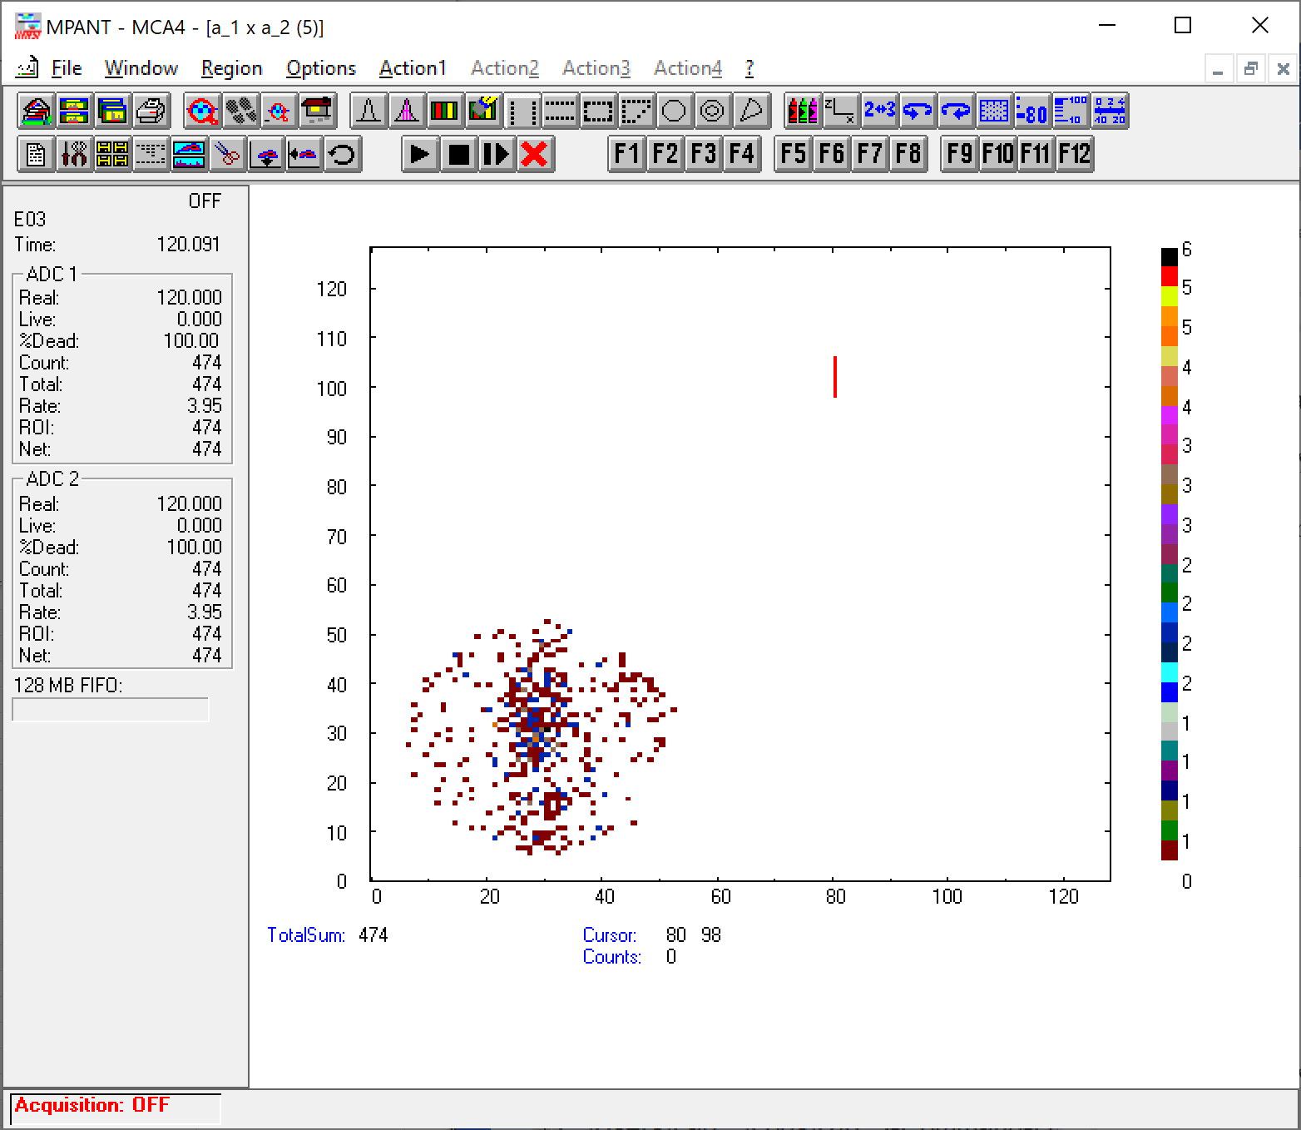
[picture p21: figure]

Changing it to 6V to see how the distribution changes. See below.

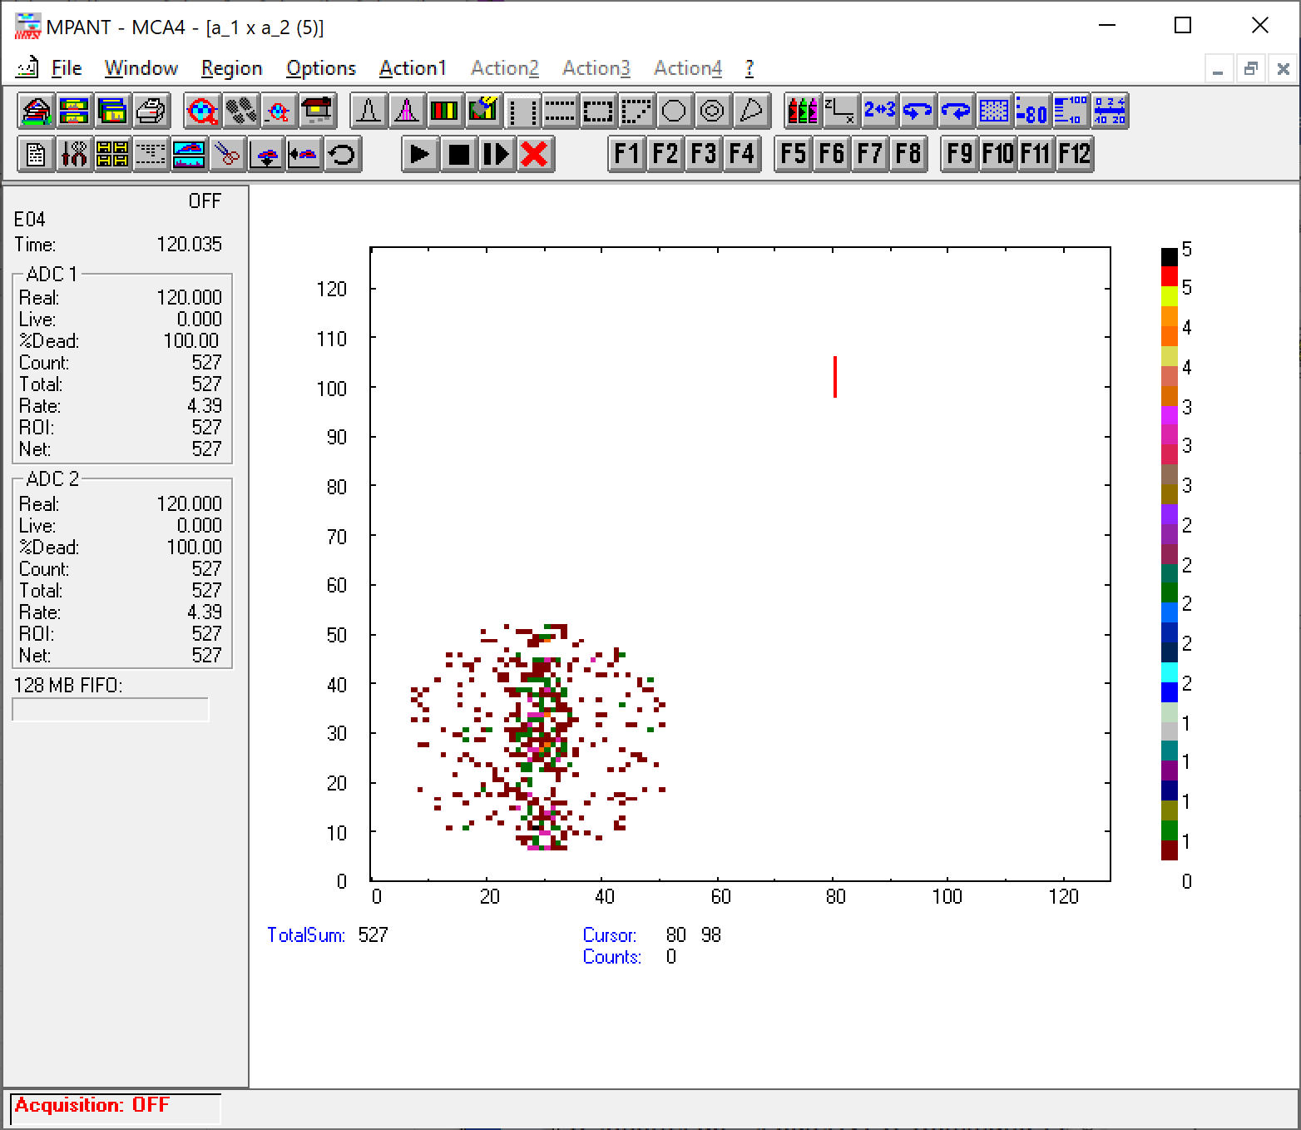
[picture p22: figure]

09:48 – LYK

Close the BL GV to change the IS pressure again to 2E-5 Torr to improve the statistics because we still don’t quite see the electrons. It could be a result of a poor statistics.

With 8V deflection plate bias:

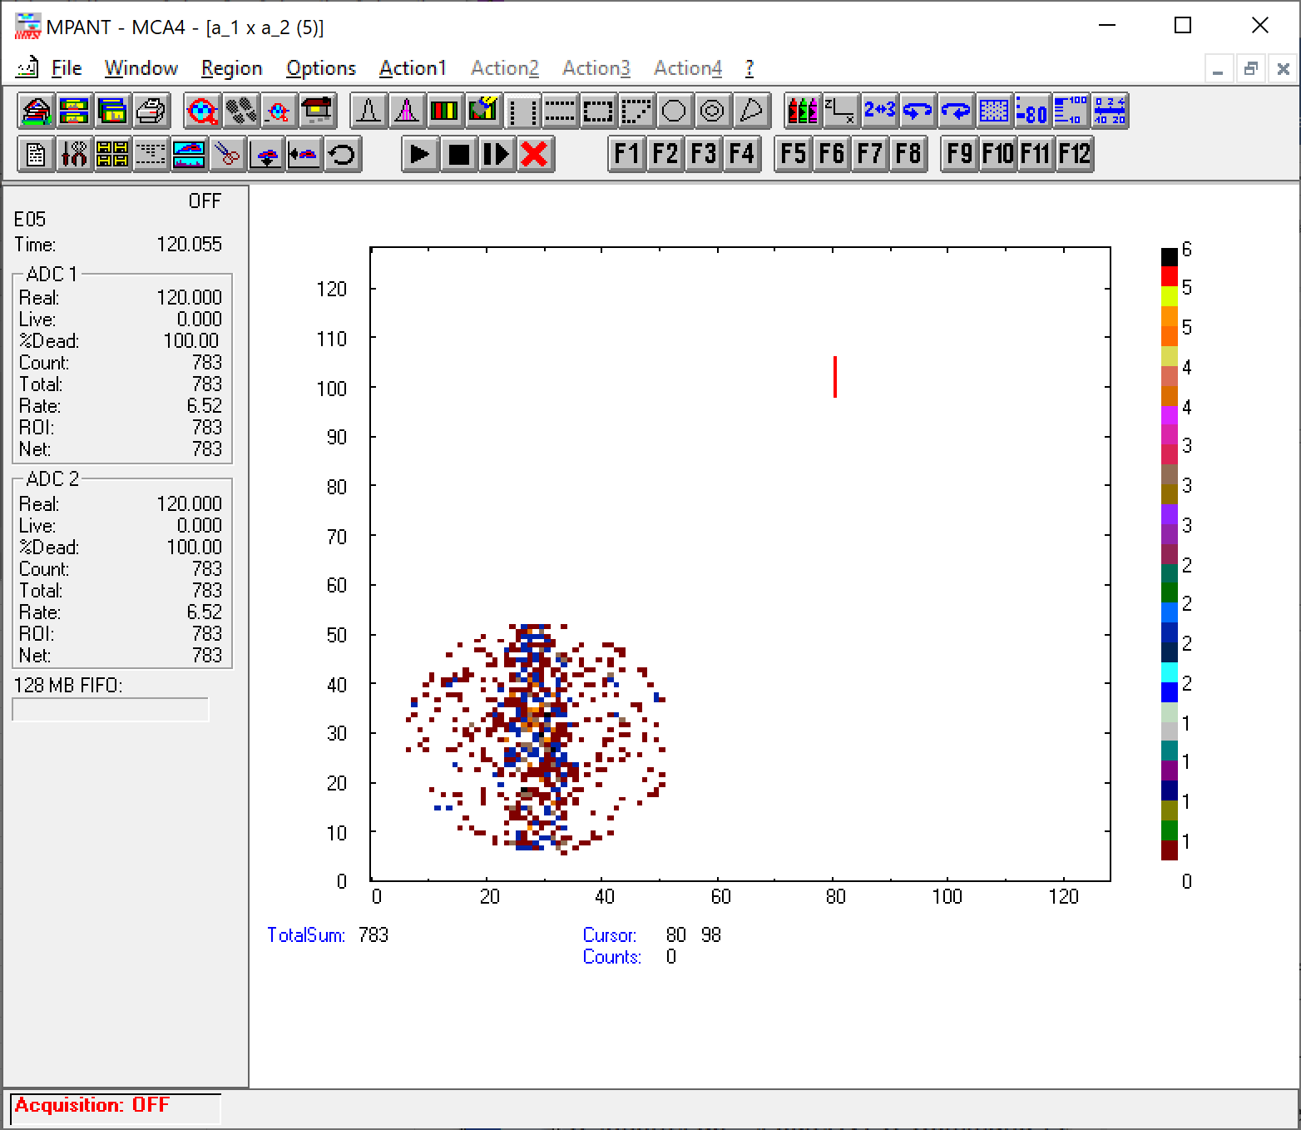
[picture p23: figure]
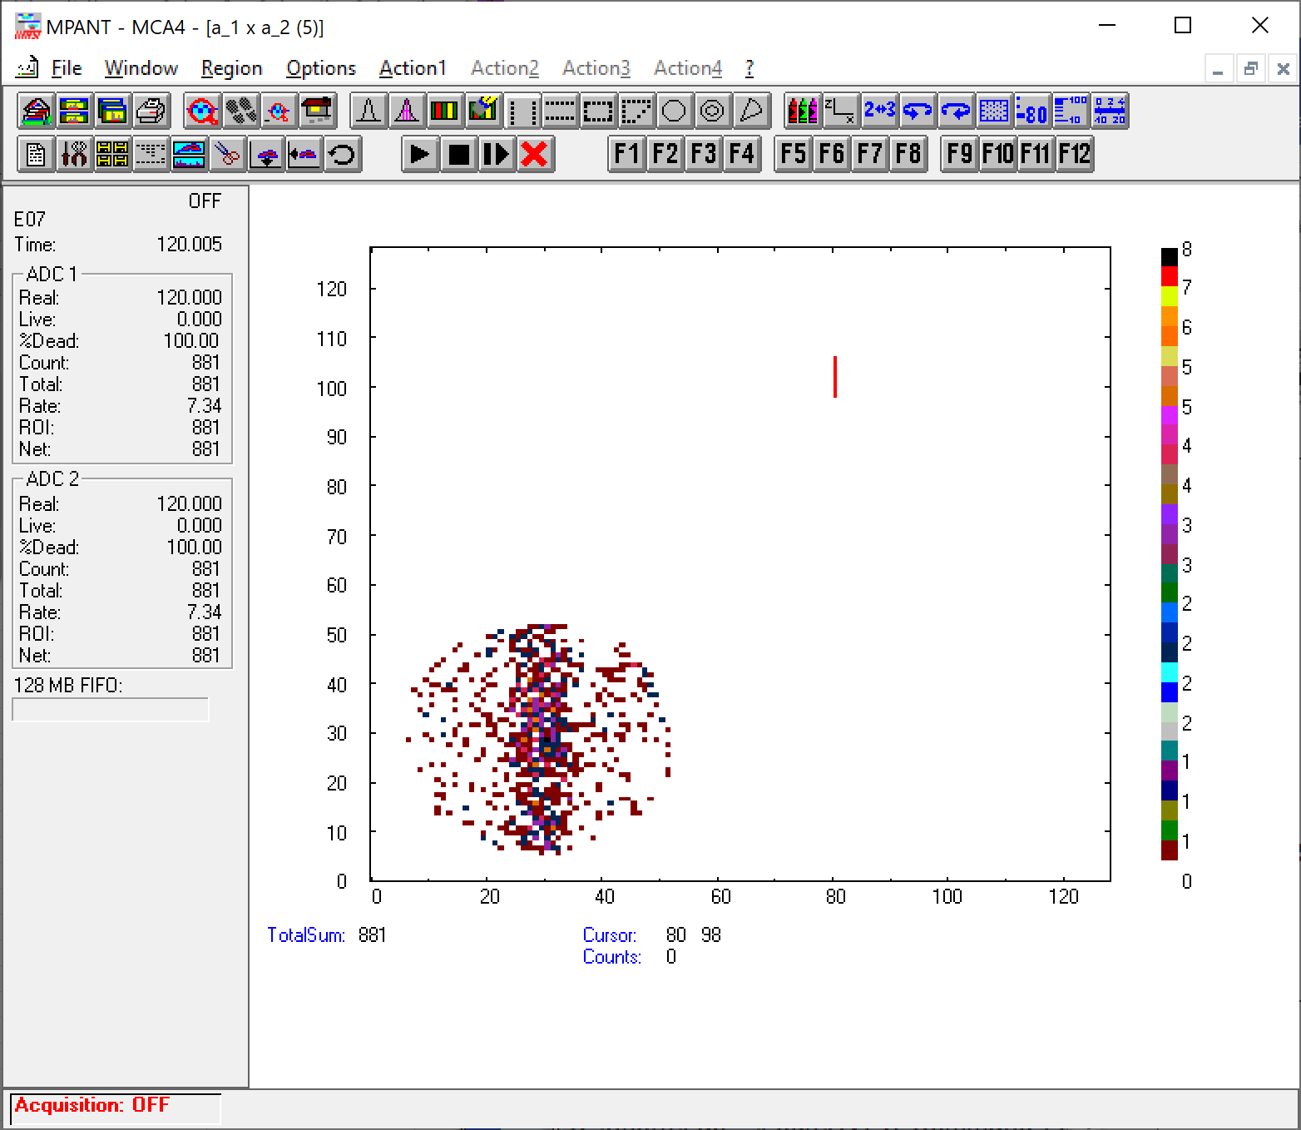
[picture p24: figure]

10:23 – LYK

Close the beamline GV to change to Graphene with deflection plate at 4V, 5V, and 6V.

10:25 – LYK
Open the beamline GV as the instrument is now at Graphene.

10:34 – LYK

Close the beamline GV to change the beam to 4keV proton. The IS pressure is at 2.3E-5 Torr. We are still at Graphene. Will repeat the test with 4keV p+ at 4, 5, 6V deflection plate.

10:35 – LYK

Open the beamline GV and start the test. Still seeing nothing, but we learn from lit search that Graphene has lower stopping power and thus lower secondary electron emission, hydrophilic (might explain why it doesn’t see the neutrals because of the thick crud layer), should generate ~the same fraction of neutrals and ions compared to amorphous carbon foil.

11:07 – LYK

Close the BL GV. We completed the electron yield tests. Maybe the statistics are low but we didn’t see the electron strips..

We should inspect the MCP after all these tests to make sure that we didn’t work the MCP too had…

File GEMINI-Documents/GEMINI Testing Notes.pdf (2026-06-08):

Day 1
Gain Curve: Filename gcXX
Going slow from 800 volts in user wait. 30 second dwell for the gain curve

During MCP gain curve, observed no outgassing

1500 V on MCP, first counts 0.2 Hz, GC08 filename. Current 0.751
Turned science chamber ion guage off.

Saving a true dark counts file as DC01 with ion gauge off in science chamber.

1675V on MCP: WE SEE THE BEAM!!!

1700V we also observe a patch at the bottom of the MCP

11:12 turned output on on HVPS. 250 V
500V

FL01 = First light, 0 V on deflector plates. 7.7 Hz FL02 = First light, 250 V on deflector plates FL03

FL11 11:58AM - GRAPHENE! 1 keV p+

After FL12 we moved the rotational stage back to Home and closed the beamline GV. Now going to dwell for 5 minutes for another dark count

We believe that the structure seen at 6 o'clock is the ion gauge

15:10 Resumed experiment

Day 2 April 24
In the lab at 8AM sharp, Lengying and I started RGA and ion source startup procedures

Ramped up MCP with the beamline GV and science chamber GV open.

Forgot to turn on Helmholtz coil

Turned on Helmholtz coil and monitored counts. Verified ~30 Hz

Turned off science chamber ion gauge at 09:13. Last reading was 1.2E-7 Torr

Plan for today:
- Dark Count test
- Carbon Foil Electron Emission 1 keV p+
- Graphene Foil Electron Emission 1 keV p+
- Carbon Foil Electron Emission 4 keV p+
- Graphene Foil Electron Emission 4 keV p+
- Carbon Foil Steering Test 4 keV p+

09:35
Closed Beamline GV and increasing pressure to 1E-5 to get better counts

Secondary electrons: We think we see a cluster maybe? But it’s hard to tell with statistics

Ramping voltage down on the deflector plates until we get to 0. Then will close the beamline GV, switch to graphene, and test at 4, 5, 6 V.

Graphene we are not seeing any structure.

Will go 6, 5, 4 V on graphene at 4 keV p+ beam. Then 6, 5, 4 V on amorphous carbon

Science Chamber Opening Tests: Be careful about cheerios. Use laser to ensure that all foils are lined up

Lengying thinks that maybe our foil floating process could be introducing water into the graphene

11:07
Ok we are switching test campaigns now. We will keep the 4 keV p+ beam but now attempt to steer the charge state populations with better statistics. Disconnected the small blue power supply and connecting the two HVPS. Will ramp to 2000 V

Jamie suggests checking the ratio of the distance of the steered dot to the 750 V to the ratio of 2500, 3000, and 3500V to the 4 keV beam. (Do this during data analysis)

YAYY we see good separation with the deflector plates! So at a 1 keV beam it’s just statistics.

UP NEXT: Shine a 16 keV beam through the graphene to try to punch through the graphene

11:30
Turning on Matsusada to float the beam up to 16 keV. Going up in 1 keV steps. Hypothesis to see what the stopping power of graphene is. Will record actual beamline voltage. Won’t save each step but just do sanity checks to see when we start seeing stuff on the MCP.

5006.20 on Total Beamline Voltage. Opening Beamline GV.About 3 Hz

Closed Beamline GV. Total Beamline Voltage: 6005.87 V. Ramping down Deflector Plates since we’re just trying to see if anything is coming through the graphene at all. Still about 3 Hz

Closed GV. Increased Total Beamline Voltage to 7006.28 V. Opened Beamline GV. Still 2-3 Hz. Completed rampdown of HVPS and powered them off.

Closed GV. Total Beamline Voltage 8006.24 V. 5 Hz now. There is no deadtime so we’re not saturating the MCP or anything. 4.88 Hz. Saving this file as G01. Ion Source Pressure 2E-5 Torr

Closed GV. Total Beamline Voltage 9004.63 V. Open Beamline GV. 5.99 Hz.

Closed GV. Total Beamline Voltage 10006.25 . Open Beamline GV. ~ 4 Hz

Closed GV. Total Beamline Voltage 11006.25 V. Open Beamline GV. 7.54 Hz

Closed GV. Total Beamline Voltage 12004.84 V. Open Beamline GV. 8.59 Hz

Closed GV. Total Beamline Voltage 13002.27 V. Open Beamline GV. 9.29 Hz

Closed GV. Total Beamline Voltage 14004.52 V. Open Beamline GV. 10.28 Hz

Closed GV. Total Beamline Voltage 15002.03 V. Open Beamline GV. Pressure is still 2E-5 Torr in the Ion Source. We see three hotspots around the perimeter of the MCP. Saving this one as G03. 11.49 Hz.

Last test. Closed Beamline GV. Total Beamline Voltage 16002.88. Open Beamline GV. 12.33 Hz. Saved as G04.

Shutting beamline down at 12:01 PM.

Look into the electrostatic properties of graphene. Maybe it’s charging up and acting as an insulator?

Dwells from this Matsusada test campaign were 120 seconds.

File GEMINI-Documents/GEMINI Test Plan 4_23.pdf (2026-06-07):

# GEMINI Test Plan 4/23

## William Li - Junior Independent Work - Spring 2026 Space Physics at Princeton

Species | Energies | Deflector Plate Target Voltage | Deflector Plate Voltage Range | Priority | Purpose
p+ | 500 eV 750 eV 1 keV 1.25 keV 1.5 keV | ± 542 V ± 813 V ± 1084 V ± 1355 V ± 1626 V | 456-629 V 684-943 V 912-1257 V 1140-1570 V 1367-1884 V | Highest | Measure angular scattering below 1 keV as a function of foil type and beam energy
p+ | 500 eV 750 eV 1 keV 1.25 keV 1.5 keV | +5 V (North) 0 V (South) | Manually tune via small blue power supply (min resolution 0.1V desired) | High | Measure secondary electron emission below 1 keV as a function of foil type and beam energy

### 3 sets of data will be gathered for each beam: (1) Baseline, (2) 0.6 μg/cm³

carbon foil, (3) graphene foil

# Proposed Tests

# Angular Scattering Deflector Plate Voltage Limits

## Absolute Maximum Limit to set in software: ± 3.8 kV

- High Voltage Qualification Testing held -3.8 kV from 11:47 AM on 4/17 to 10:26 AM on 4/18
- Since only testing beam energies of 1.5 keV or lower, the maximum anticipated voltage is 1884 V (see Slide 2)

Other High Voltage Qualification Test Results
- 4/8 16:38 - 17:34 at -4.5 kV (56 minutes before trip)
- 4/8 19:07 - 19:29 at -4.5 kV (22 minutes before trip)
- 4/9 09:06 - 13:36 at -4.5 kV (4 hours 30 minutes before trip)
- 4/9 13:56 - 14:16 at -4.5 kV (20 minutes before trip)
- 4/9 16:30 - 4/10 02:11 at -4 kV (9 hours 41 minutes before trip)

Reworked MCP Bracket and polished Deflector Plates
- 4/17 17:43 - 19:28 at -4 kV (1 hr 45 minutes before trip)
- 4/18 11:47 - 4/19 10:26 at -3.8 kV (22 hrs 39 minutes before trip)

# Angular Scattering Deflector Plate Voltage Lookup Graph

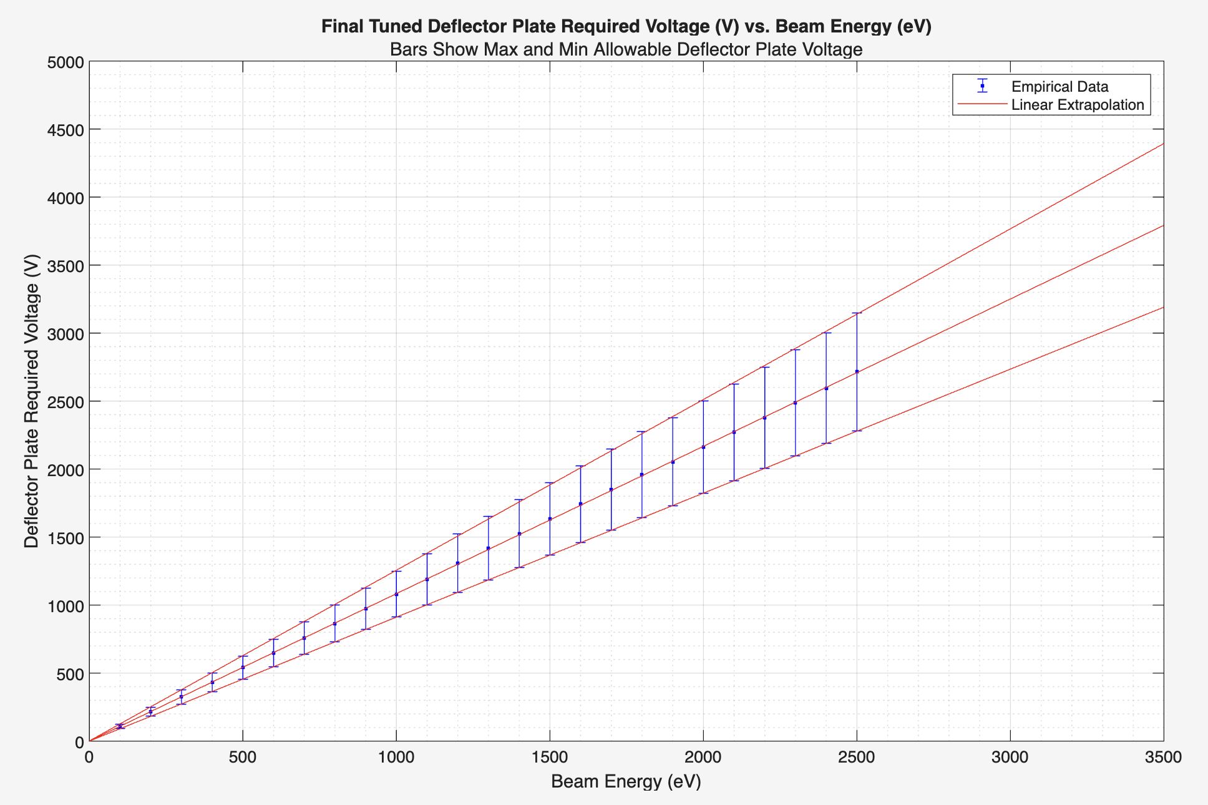
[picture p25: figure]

# Angular Scattering Deflector Plate Voltage Lookup Table

Energy | Target Voltage (V) | Min Voltage (V) | Max Voltage (V)
500 eV | ± 542 | 456 | 629
750 eV | ± 813 | 684 | 943
1 keV | ± 1084 | 912 | 1257
1.25 keV | ± 1355 | 1140 | 1570
1.5 keV | ± 1626 | 1367 | 1884

Deflector Plate voltage is only a function of beam energy, not species

# Dwell Time

Concern: Pinhole will result in high counts/area on the face of the Quantar MCP

Pinhole area was not measured prior to installation in the Science Chamber but has a minimum diameter of 1.75mm based on drill size used during manufacturing

Pinhole Diameter: 1.75 mm → 2.4 mm²
Pinhole Area
MCP Diameter: 40 mm → 1256.6 mm²
MCP Area

Count rate on MCP = (MCP Area/100)*Pinhole Area = 30.2 Hz
- 100 based on MCP allowable parameters?

If t = dwell time, precision = sqrt(N)/N = sqrt(30.2Hz*t)/(30.2Hz*t)
- t = 120s gives 1.7%

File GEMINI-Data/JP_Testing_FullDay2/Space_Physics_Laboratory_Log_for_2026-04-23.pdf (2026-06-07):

### Space Physics Laboratory Logbook Princeton University - 171 Broadmead

April 23, 2026 (Thursday)

07:58 – LYK

Open the lab with William. We are going to start the RGA and ion source ignition.

08:06 – JSR

Ion source supplies powered on. Ion source pressure jumped from 1.8E-8 to 9.5E-7 torr. Not a bad spike.

08:45 – JSR

Eek! It looks like there’s a contamination in the science chamber from the previous tests. That and the pressure is a bit higher than normal since we were only going off of the turbo. We’ll probably need to spend time cleaning the chambers and back-filling with nitrogen once we take William’s experiment out.

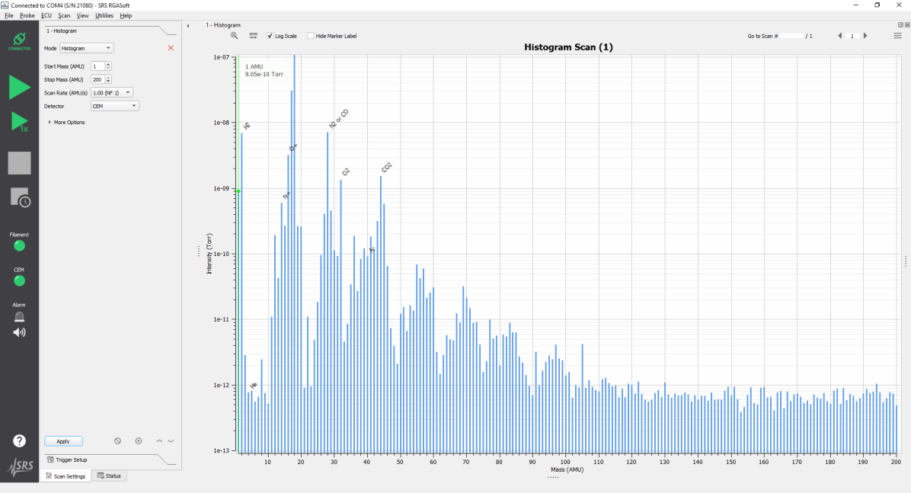
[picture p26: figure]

08:51 – JSR

Main Chamber pressure = 3.7E-8 torr. Science Chamber pressure = 1.9E-7 torr. I opened the Main Chamber GV so we could let the East and West Cryos help lower the science chamber pressure.

08:52 – JSR

For reference, see below for the RGA scan of the science chamber after the sapphire ring team installed their project.

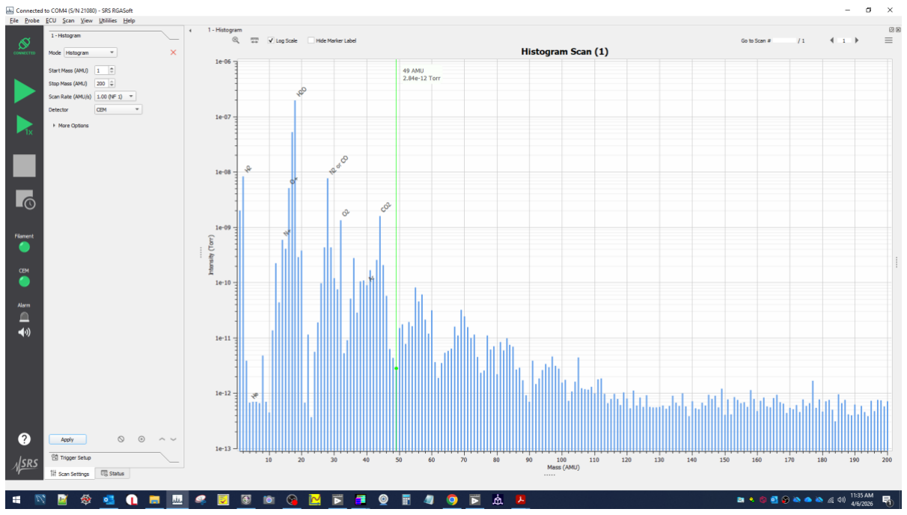
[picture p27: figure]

08:57 – JSR

William asked an excellent question: “what is sapphire made of?” Turns out it’s a variant of aluminum oxide (Al2O3) which gives it a molar mass of 2 x 27 + 3 x 16 = 102. This makes that lone spike there awfully suspicious. Anyhow, good to know for later.

09:02 – JSR

I’m closing the p-leak down to target ~5E-7 torr for the

09:34 – WJL

Lengying opened the science chamber gate valve. Science chamber pressure was 1.37E-7 Torr.

09:42 – WJL

Jamie removed the ABM aft cone SHV-5 cable. This is for the ABM 40V bias plate. We are borrowing it for William Li’s GEMINI experiment. This belongs in the bottom port of the ABM bias plate.

09:51 – LYK

Ready to ramp up MCP to 800 V. The SC pressure is at 1.2E-7 Torr we are going to park the MCP at low voltage to allow outgassing and hopefully allowing the SC pressure to go down.

09:56 – LYK

We are at 800 V for MCP. SC pressure is 1.2E-7 Torr; MC: 4.3E-8 Torr

We will let the MCP sit here for a while.

10:07 – JSR

Pressure is 1.19E-7 torr in the science chamber. Based on the current trends, William and I discerned that it probably won’t dip below 1.0E-7 for at least another 3 hours. Therefore, we will proceed, but with caution:

1) We will slowly ramp the MCP voltage when the time comes (currently at 800 V and 0.399 mA).
2) We will drop the ion source pressure (currently at 8E-7, target will be 5E-7 torr)
3) We will look for any signs of outgassing (little pressure spikes) in the science chamber along the way.

10:13 – JSR

I adjusted the P-Leak down to 34,250 steps which puts the ion source pressure at 5E-7 torr.

10:23 – JSR

We’re at 1100 V and no pressure spikes in the science chamber or dark counts in the MCP, which is as expected (anticipated “dark counts” should start around 1400 V). We still have the beamline GV closed. We will open this after we see dark counts.

10:28 – JSR

We still did not see any counts with 1400 V on the MCP. We’ve seen no spikes in the science chamber so far…

10:32 – JSR

We saw our first counts at 1500 V on the MCP. Current is 0.751 mA. These weren’t completely “dark” because the science chamber ion gauge was on. We saw 0.2 Hz (6 counts in 30 sec) and saved this file as “GC08”. Now we’re going to make the true dark counts file and save it as “DC01”.

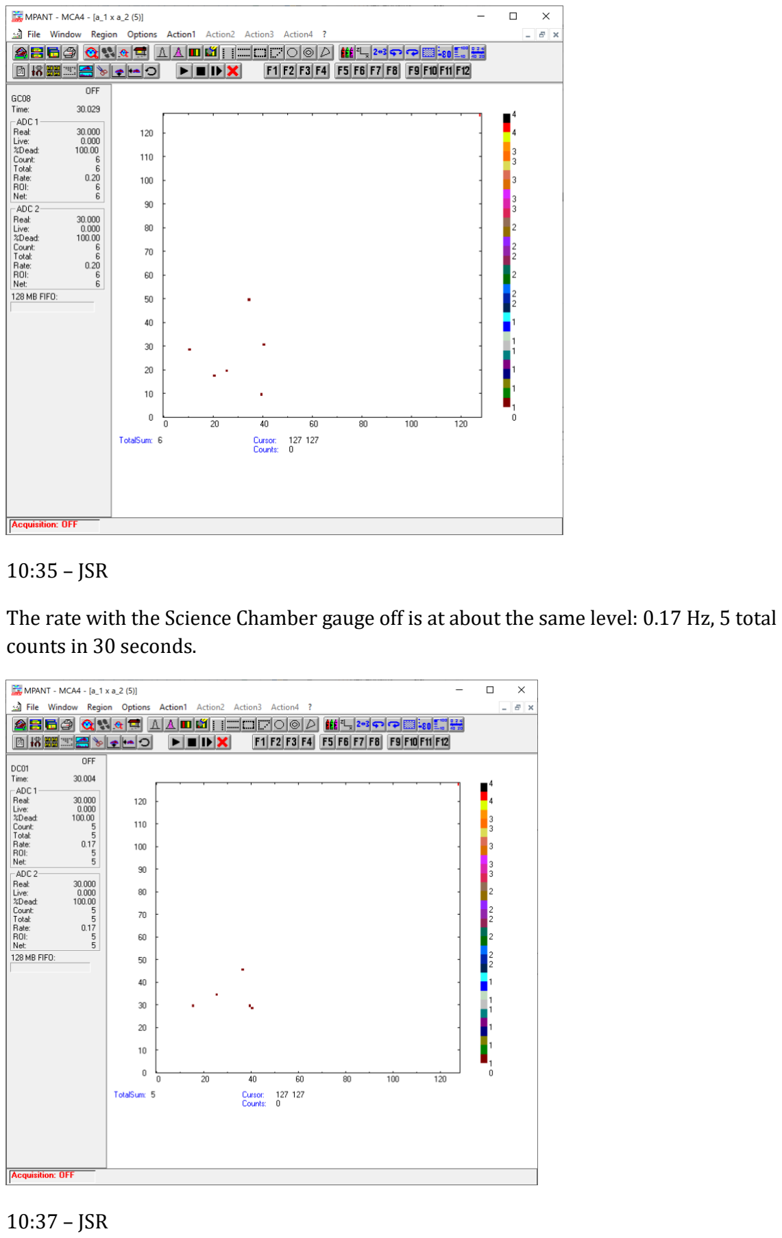
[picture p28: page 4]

10:35 – JSR

The rate with the Science Chamber gauge off is at about the same level: 0.17 Hz, 5 total counts in 30 seconds.

10:37 – JSR

I opened the beamline GV. I think we’ll need to turn the science chamber gauge back on because we’ll need to make sure we don’t have any discharge events throughout these tests (including when William applies voltage to the GEMINI deflector plates). It doesn’t seem like the gauge is contributing much (if at all) to the dark counts rate anyway.

10:39 – JSR

We saved file “T01” to capture this data at 1500 V on the MCP, 0.751 mA current, beamline GV open, Ion source Pressure = 4.98E-7 torr, Ion Turbo Pressure is at 1.94E-9 torr.

Total counts were: 2 in 30 seconds, which corresponds to a rate of 0.07 Hz.

10:48 – JSR

We’re proceeding with the ramp up. 1600 V on the MCP with a current of 0.801 mA. We saw 11 total counts (0.37 Hz), so maybe we’re getting some of the beam (file GC09). Now I’m turning on the science chamber ion gauge. William is also carefully recording this gain curve test in the spreadsheet. At some point, we should see the beam emerge through the pinhole from the GEMINI apparatus. I’ll log that “first light” result.

11:11 – JSR

Gain curve tests complete. 1800 V is where we’ll target on the MCP today. That gave us a 14.5 Hz rate. The current was similar to previous operations of the MCP.

11:15 – JSR

First light! Hooray! Deflector power supplies are powered on, but at their lowest setting (in this case -37 V and +39 V. Currents are 0.000 to 0.001 mA. These data are saved in “FL01”.

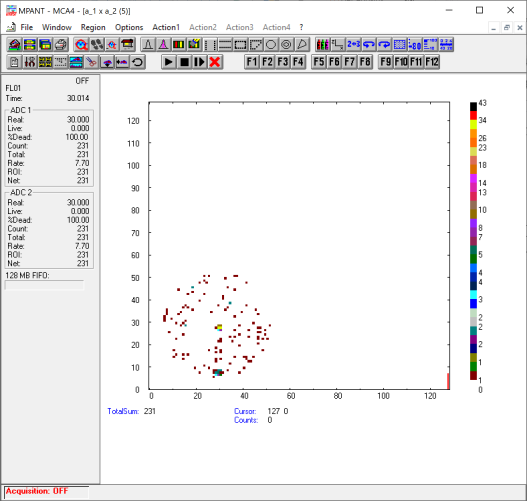
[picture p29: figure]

11:23 – JSR

Hooray! At +/-250 V on the deflectors, William steered the proton beam! Looks like it moved ~5 mm.

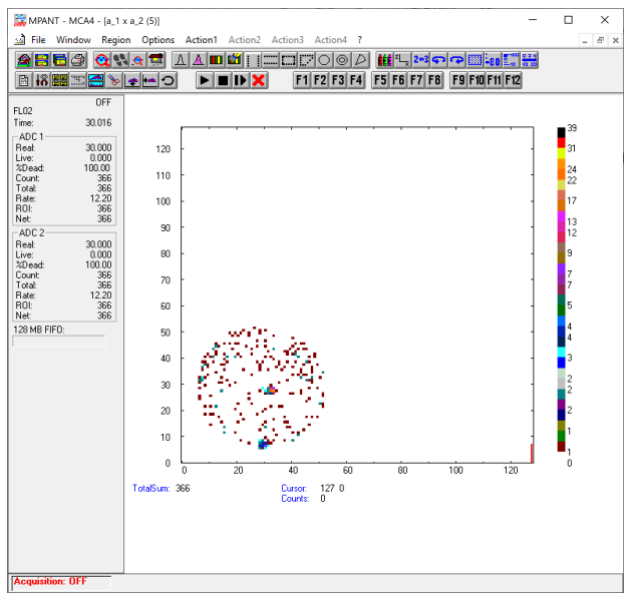
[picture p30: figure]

11:27 – JSR

William steered the beam again, with the dot now centered at around 38 mm, but there’s A LOT more scattering, so the actually pinpoint is hard to see.


11:34 – JSR

At William’s target deflector voltages (+/-1083 V), the proton beam has moved to the edge of the MCP, exactly as William intended. Hooray! There is a lot of scattering. Some of it could be due to the neutral beam contamination. But right now we’re going through the open aperture. Maybe a chunk of this will be eliminated


12:11 – JSR

We took “dark counts” with the beamline GV closed but science chamber ion gauge on, so maybe that odd “structure” we see (and the scattering) can be explained by the ion gauge! Oops. That would explain a lot. We saved this in file DC02.


12:15 – JSR

I turned off the science chamber ion gauge. Starting “DC03” which should reflect the real dark counts now.

12:20 – JSR

I tweaked the P-leak to 37,000 steps.

12:26 – JSR

We re-opened the beamline GV. IS = 1.0E-6 torr. IT = 3.6E-9 torr. Deflectors at +/-1084 V. The stage is rotated to amorphous carbon (54.12 deg). This might be the actual real first light!

13:03 – LYK

Close the beamline GV twice. Once to change the IS pressure to 5E-6 Torr. Now at IS = 1E-5 Torr.

13:13 – LYK

At 2E-5 Torr, we saw about 5 Hz. That means with 120 second dwell, the uncertainty is ~5%.


We set the deflection plate to 0 V and ramp MCP down to 1400 V. Turn on the SC ion gauge to monitor the status.

13:20 – LYK

Students are still in the lab. Will ask Ted to cover me while I have a lunch break.

15:09 – JSR

Back to William’s GEMINI measurements. I turned off the gauge and ramped up the Quantar MCP back to 1800 V (current = 0.902 mA). William set his deflector voltages to +/-750 volts. The stage is currently on the amorphous carbon.

15:15 – JSR

I opened the beamline GV. Let the testing resume!

15:18 – JSR

Here’s the result with deflectors at +/-750 volts and Ion source pressure at 1.7E-5 torr.


15:26 – JSR

Here’s the result with deflectors at +/-500 volts and Ion source pressure at 1.7E-5 torr.


15:29 – JSR

Here’s the result with deflectors at +/-250 volts and Ion source pressure at 1.7E-5 torr (FL22).


15:35 – JSR

Here’s the result with deflectors at +/-0 volts (in practice, +39 and -28 V) and Ion source pressure at 1.7E-5 torr (FL23). Hmm. I mean, maybe the “hot spot” feature is different?

But the distribution doesn’t seem to have moved.


15:40 – JSR

Here’s the result with deflectors at +/-1250 volts and Ion source pressure at 1.7E-5 torr (FL24).


15:45 – JSR

Here’s the result with deflectors at +/-2000 volts and Ion source pressure at 1.7E-5 torr (FL25). This should have completely deflected the negative and positive charges away…so have we just been seeing neutrals the whole time?


15:49 – JSR

Same settings, but with HC off.

So the ion beam is the incident cause of the stripe, but we don’t quite understand what’s happening on the back end…

15:50 – JSR

I closed the beamline GV. We’re going to rotate on to the graphene foil.

15:55 – JSR

I opened the beamline GV and we started measurements on the graphene foil with the ion source pressure at 1.66E-5 torr and ion turbo pressure at 5.63E-8 torr. Oops – had to also turn the HC back on too. 😉

16:00 – JSR

Well…here’s our very first measurements with a graphene foil! The results are quite…puzzling! Plates are set at +/-1084 V. Nothing else has changed other than the foil.


16:01 – JSR

No obvious change with the plates set to +/-160 V.


16:09 – JSR

Wow. With 0 dialed in on the plates, we get something close to dark counts. Could the graphene be blocking the 1 keV particles nearly completely?


16:14 -- JSR

We closed the beamline GV and dialed in 4 keV protons. We won’t be using any deflector voltages here, but this will tell us if we can get any part of the beam through the graphene foil at all!

16:18 – JSR

No beam through the graphene!


16:25 – JSR

We were so puzzled that we closed the beamline GV, left everything else untouched and only rotated the amorphous carbon foil into the beam. Here’s what we got from the acquired data. There’s obviously a beam going through AND the scattering ellipse is smaller than the diameter of the MCP, which is what theory would predict.


16:29 – JSR

I changed the beam energy back down to target 1 keV protons.

16:33 – JSR

We kept the deflectors at 0 V (really -29 and +39 V) and saw the usual stripe come back (FL32):


The rate is consistent with what we previously measured in this configuration (5.81 Hz; FL23).

16:34 – JSR

Lastly, per William’s request, we’re going to drop the pressures (currently IT = 1.6E-5 torr, IS = 5.6E-8 torr) and get back to some safe low value to confirm that the deflectors do, in fact, steer the pinhole beam (no foil configuration).

16:38 – JSR

I brought the ion source pressure down to 1.1E-6 torr. I’ll put it a little below that (targeting 7.5E-7 torr), but a little higher than this morning (5E-7 torr).

16:41 – JSR

P-Leak now at 34,750 steps. Ion source pressure between 7.3 and 7.5E-7 torr.

16:42 – JSR

William opened the beamline GV. FL33 captures the dot (same as this morning) with 0 V on the deflectors.


16:42 – JSR

FL34 captures the beam dot location with +/1084 V on the deflectors. So the deflectors are clearly moving the beam! Maybe in this case there’s some scattering at the edges. And there does appear to be a neutral component coming through as well.


16:48 – JSR

Okay! One final deflector setting (+/-750 V; FL35) through the pinhole (no foils) and this indeed confirms we are properly steering the beam (without a foil, anyway).


17:02 – WJL

Lengying turned off the high voltage power supply on the ion source. We turned the science chamber ion gauge back on. The science chamber pressure is 2.2E-7 Torr.

17:41 – JSR

Ion Source, Deflector plates, HC, MCP power supplies are all powered down. We’re leaving the Main Chamber GV open to help bring the science chamber to lower pressures.

17:43 – JSR

Time to close the lab.

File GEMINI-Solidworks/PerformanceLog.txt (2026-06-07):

Number of Contacts: 1
Number of contact data: 1073

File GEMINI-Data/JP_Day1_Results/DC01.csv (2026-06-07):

[DISPLAY]
VER=244
TYPE=1
DATALEN=2
XPARAM=0
YPARAM=1
XRANGE=127
YRANGE=127
NAME=a_1 x a_2
XTITLE=a_1
YTITLE=a_2
[DATA]
40	28	1
15	29	1
39	29	1
25	34	1
36	45	1

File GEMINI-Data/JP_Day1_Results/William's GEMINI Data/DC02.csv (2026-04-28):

[DISPLAY]
VER=244
TYPE=1
DATALEN=2
XPARAM=0
YPARAM=1
XRANGE=127
YRANGE=127
NAME=a_1 x a_2
XTITLE=a_1
YTITLE=a_2
[DATA]
27 | 5 | 1
28 | 5 | 6
29 | 5 | 14
30 | 5 | 20
31 | 5 | 6
32 | 5 | 1
24 | 6 | 2
25 | 6 | 5
26 | 6 | 1
27 | 6 | 5
28 | 6 | 45
29 | 6 | 111
30 | 6 | 92
31 | 6 | 37
32 | 6 | 9
33 | 6 | 2
22 | 7 | 1
23 | 7 | 4
24 | 7 | 1
25 | 7 | 2
26 | 7 | 1
27 | 7 | 11
28 | 7 | 28
29 | 7 | 72
30 | 7 | 55
31 | 7 | 15
32 | 7 | 4
33 | 7 | 1
34 | 7 | 1
36 | 7 | 4
37 | 7 | 1
39 | 7 | 1
18 | 8 | 1
19 | 8 | 1
22 | 8 | 1
23 | 8 | 1
25 | 8 | 2
26 | 8 | 1
27 | 8 | 6
28 | 8 | 13
29 | 8 | 17
30 | 8 | 21
31 | 8 | 4
32 | 8 | 2
34 | 8 | 2
36 | 8 | 2
37 | 8 | 1
38 | 8 | 1
17 | 9 | 2
18 | 9 | 2
20 | 9 | 1
21 | 9 | 1
23 | 9 | 2
28 | 9 | 2
29 | 9 | 5
30 | 9 | 7
31 | 9 | 2
34 | 9 | 3
35 | 9 | 2
36 | 9 | 2
37 | 9 | 1
40 | 9 | 1
41 | 9 | 2
42 | 9 | 1
15 | 10 | 1
16 | 10 | 2
19 | 10 | 1
20 | 10 | 1
21 | 10 | 1
22 | 10 | 1
26 | 10 | 1
27 | 10 | 1
28 | 10 | 2
29 | 10 | 2
31 | 10 | 1
33 | 10 | 1
34 | 10 | 1
36 | 10 | 1
38 | 10 | 1
39 | 10 | 1
41 | 10 | 2
42 | 10 | 1
13 | 11 | 1
23 | 11 | 2
24 | 11 | 1
25 | 11 | 1
26 | 11 | 2
27 | 11 | 1
29 | 11 | 3
32 | 11 | 1
33 | 11 | 1
36 | 11 | 2
37 | 11 | 3
39 | 11 | 2
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

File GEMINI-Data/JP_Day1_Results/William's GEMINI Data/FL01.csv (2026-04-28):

[DISPLAY]
VER=244
TYPE=1
DATALEN=2
XPARAM=0
YPARAM=1
XRANGE=127
YRANGE=127
NAME=a_1 x a_2
XTITLE=a_1
YTITLE=a_2
[DATA]
29 | 5 | 3
30 | 5 | 3
27 | 6 | 1
28 | 6 | 5
29 | 6 | 10
30 | 6 | 5
31 | 6 | 1
28 | 7 | 3
29 | 7 | 4
30 | 7 | 3
31 | 7 | 1
32 | 7 | 1
37 | 7 | 1
39 | 7 | 1
20 | 8 | 1
26 | 8 | 1
29 | 8 | 2
30 | 8 | 3
34 | 8 | 1
38 | 8 | 1
31 | 9 | 1
40 | 9 | 2
16 | 10 | 1
37 | 10 | 1
32 | 11 | 1
40 | 11 | 1
27 | 12 | 1
28 | 12 | 1
34 | 12 | 1
38 | 12 | 1
43 | 12 | 1
12 | 13 | 1
13 | 13 | 1
33 | 13 | 1
45 | 13 | 2
14 | 14 | 1
40 | 14 | 1
19 | 15 | 1
21 | 15 | 1
34 | 15 | 1
45 | 15 | 1
10 | 18 | 1
46 | 18 | 1
38 | 19 | 2
29 | 20 | 1
30 | 20 | 1
42 | 20 | 1
43 | 20 | 1
49 | 20 | 1
16 | 21 | 2
17 | 21 | 1
23 | 21 | 1
28 | 21 | 1
34 | 21 | 1
42 | 21 | 1
43 | 21 | 1
51 | 21 | 1
9 | 22 | 1
17 | 22 | 1
30 | 22 | 1
42 | 22 | 1
48 | 22 | 1
16 | 23 | 2
21 | 23 | 1
35 | 23 | 1
48 | 23 | 1
7 | 24 | 1
32 | 24 | 1
49 | 24 | 1
9 | 25 | 1
11 | 25 | 1
20 | 25 | 1
31 | 25 | 1
33 | 25 | 2
43 | 25 | 1
44 | 25 | 1
48 | 25 | 1
50 | 25 | 1
51 | 25 | 1
9 | 26 | 1
29 | 26 | 2
32 | 26 | 3
33 | 26 | 5
37 | 26 | 3
48 | 26 | 1
50 | 26 | 1
29 | 27 | 4
30 | 27 | 2
31 | 27 | 2
32 | 27 | 23
33 | 27 | 18
34 | 27 | 1
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

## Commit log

2026-01-15 SolidWorks Files
    [7113K148_Ring Terminals.SLDPRT, 8974K105_Multipurpose 6061 Aluminum Rod.SLDPRT, 90550A122_Vented Flat Head Screw.SLDPRT, 90585A283_316 Stainless Steel Hex Driv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]
2026-01-15 Final Drawing Package
    [8974K105_Multipurpose 6061 Aluminum Rod.SLDDRW, 91780A189_Female Threaded Hex Standoff.SLDDRW, 91780A189_Female Threaded Hex Standoff.SLDPRT, 93330A541_Female 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]
2026-01-16 Drawing package update
    [ROTATIONAL_SPACER_SHIM.SLDDRW]
2026-04-28 Uploading GEMINI Data
    [DC02.csv, DC03.csv, DC04.csv, E01.csv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]
2026-06-07 Reorganization to send to Dan for archiving
    [2464K1_Clamping Precision Flexible Shaft Coupling.STL, 7113K148_Ring Terminals.SLDPRT, 8974K105_Multipurpose 6061 Aluminum Rod.SLDDRW, 8974K105_Multipurpose 60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]
2026-06-07 Adding files from Mac for GEMINI Archive
    [3mmKnifeEdgeDisk.stp, ABM_GRID.3mf, ABM_GRID.STL, APERTURE_PLATE_FULL.STL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]
2026-06-08 Adding final documents (minus assembly procedure)
